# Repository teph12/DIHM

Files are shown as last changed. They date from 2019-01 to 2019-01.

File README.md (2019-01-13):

Digital Inline Holographic Microscopy (DIHM)
===========================================

Here we want to present an easy to use digital inline holographic microscope employing 3D printed parts, a Raspberry Pi and Pi Cam, as well as a high-power LED and a 15 micron pinhole. For details see (link to publication following).

# Assembly

1. Print the required parts (.stl files) with a 3D printer or a 3D-printing service of your choice. We used PLA as printer material. 
2. Using pliers, remove the lens in front of the Raspberry Pi Cam v2. Assemble the Raspberry Pi 3 and the Raspberry Pi Cam.  
3. Fix the pinhole on the upper side of the pinhole holder. We used black tape to prevent residual light from passing. 
4. Connect the LED to a current source providing a current of 125 mA. Run the cables through the hole in the lower box. Fix the LED on the lower side of the pinhole holder.
5. Assemble lower box, pinhole holder and upper box. Connect the Raspberry Pi Cam to the upper box. Connect a monitor, mouse and power source to the Raspberry Pi. Power it on.

# Image Acquisition

1. Open Camera_DIHM.py and insert the experimental parameters. If you run the file, a folder with the name YY.MM.DD_hh.mm will be created and all following files will be saved here. 
ATTENTION: Run Camera_DIHM.py only once every minute, or the previous files will be overwritten!
2. If you control the LED with the Raspberry Pi's GPIO, it will now be turned on. If not, turn on the LED. 
3. Insert an object on a standard microscope slide. You will now see its hologram in the preview.
4. By pressing ENTER an image of the object is captured. If you want to capture a higher number of images, you can enter the number in range(N).
5. Remove the object slide. By pressing ENTER again, N in range(N) background images are captured.

# Reconstruction

1. Move the images to a PC with Fiji and the following plugin installed https://unal-optodigital.github.io/NumericalPropagation/
2. Open Fiji and the plugin.
3. Open the object image and choose Image>Type>32-Bit to convert it to a greyscale image.
4. In the Plugin choose the image as real image. Let imaginary image empty. Enter the required parameters.
5. Press propagate. After that, you can reconstruct several image planes at once by using Batch. To increase the reconstructed image's contrast you can use Process>Enhance Contrast with (0.2, normalize, prozess whole stack).

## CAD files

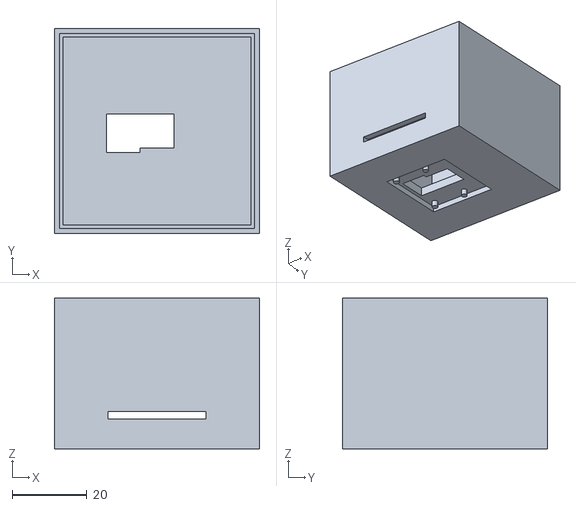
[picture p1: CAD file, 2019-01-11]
Upper_Box.stl
55.0 x 55.0 x 40.5

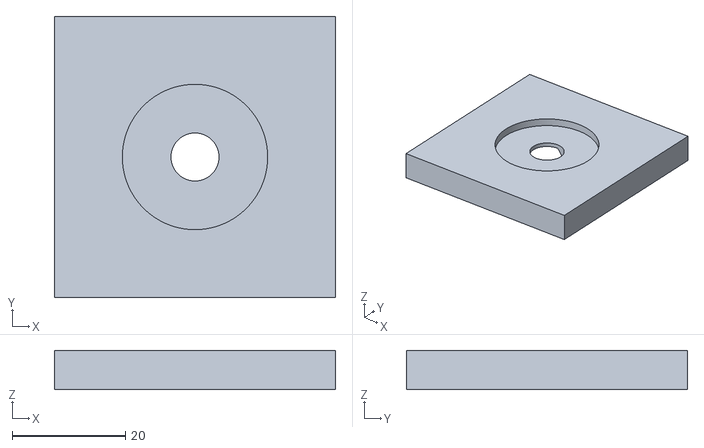
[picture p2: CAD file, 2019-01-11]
Pinhole_Holder.stl
49.7 x 49.7 x 6.90

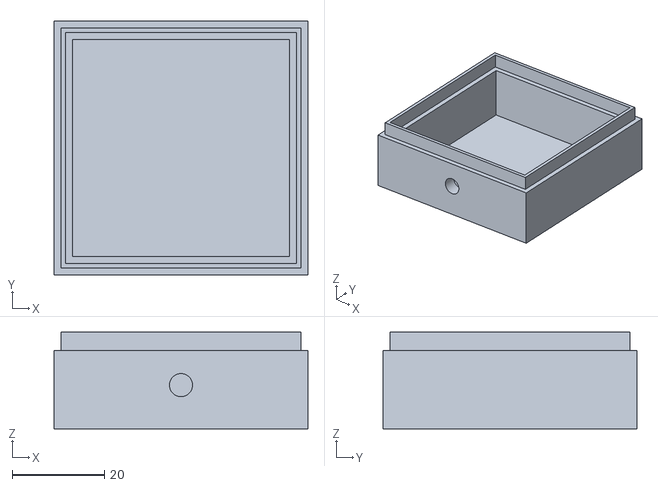
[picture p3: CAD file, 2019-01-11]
Lower_Box.stl
55.0 x 55.0 x 21.0

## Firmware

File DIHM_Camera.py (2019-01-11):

import os
import errno
import picamera
import time
import RPi.GPIO as GPIO

#initialize GPIO

GPIO.setmode(GPIO.BCM)
GPIO.setup(17, GPIO.OUT)


#initialize parameters

d1 = 30     	#distance between pinhole and camera in mm
d2 = 5.91     	#distance between object and camera in mm
ph = 15       	#pinhole size in microns
wl = 430      	#wavelength in nm
object = 'objectname' #which object

#create the directory and save the parameters

path = "/home/pi/Desktop/" + time.strftime("%y.%m.%d_%H.%M") #the absolute path
filename = path + "/Parameters.txt" #the folder is named after the current date and time. If you take several pictures in one minute, they get overwritten!
if not os.path.exists(os.path.dirname(filename)):
    try: os.makedirs(os.path.dirname(filename))
    except OSError as exc: # Guard against race condition
        if exc.errno != errno.EEXIST:
            raise

with open(filename, "w") as f:  #write down experimental parameters
    f.write("Object: " + object +"\r")
    f.write("Distance between camera and pinhole: " + str(d1) + " mm\r")
    f.write("Distance between camera and object: " + str(d2) + " mm\r")
    f.write("Pinhole size: " + str(ph) + " microns\r")
    f.write("Wavelength: " + str(wl) + " nm\r")

#turn on LED and capture images
    
GPIO.output(17, GPIO.HIGH)  #turns on LED 

with picamera.PiCamera() as camera:
    camera.resolution = (3280, 2464)    
    camera.iso = 100    #fixed iso
    camera.awb_mode = 'off'     
    camera.awb_gains = (1,3)    #fixed white balance
    camera.start_preview(resolution=(1440, 1080))
    input("Take Picture")
    camera.capture_sequence([path + '/object%s.jpg'%i for i in range(1)])   #one image is captured on pressing enter
    input("Take Background")
    camera.capture_sequence([path + '/background%s.jpg'%i for i in range(1)]) #remove object. On pressing enter again, the background image is captured.
    camera.close()
    

GPIO.output(17, GPIO.LOW)   #turns off LED

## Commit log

2019-01-11 Add files via upload
    .stl files for 3D-printing the DIHM housing
    [Lower_Box.stl, Pinhole_Holder.stl, Upper_Box.stl]
2019-02-12 Updated Camera.py
    Updated Camera.py with correct tabs and line breaks
